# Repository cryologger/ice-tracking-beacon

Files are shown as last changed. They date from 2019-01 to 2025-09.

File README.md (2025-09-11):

# Cryologger - Iceberg Tracking Beacon (ITB)





### Note: This project is under active development. 



## 1.0 Introduction
Icebergs and ice islands represent significant hazards to marine navigation and offshore infrastructure at a time when demand for access to Canada’s Arctic waters is increasing. There is a growing demand for in situ iceberg tracking data to monitor their drift trajectory and improve predictions of ice hazard occurrence and behaviour, yet the high cost of commercial tracking devices often prevents monitoring at optimal spatial and temporal resolutions.

The Cryologger Ice Tracking Beacon (ITB), built using inexpensive, open-source hardware and software, provides a reliable and cost-effective platform for monitoring the drift of icebergs and ice islands in the Canadian Arctic.

## 2.0 Methods

### 2.1 Design

The Cryologger ITB is based on the open-source Arduino platform (www.arduino.cc) and built using low-cost, do-it-yourself electronics that can be easily modified to meet the needs of the end-user. Code was written using the Arduino Integrated Development Environment (IDE) and benefits from the availability of community-generated libraries.

Planned for extended deployments in harsh Arctic conditions, the Cryologger ITB provides long-term measurements of GNSS position, temperature, pressure, pitch, roll, tilt-compensated heading and battery voltage. Data are transmitted over the Iridium satellite network at specified intervals and can be remotely updated based on the desired sampling frequency. Collected data are made available in near-real time at https://cryologger.org.

#### 2.1.1 Design Iterations

More information about the design of versions 1.0 and 2.0 of the Cryologger ITB can be found in the following publication:

[Garbo, A., & Mueller, D. (2024). Cryologger Ice Tracking Beacon: A Low-Cost, Open-Source Platform for Tracking Icebergs and Ice Islands. _Sensors_, _24_(4), Article 4. https://doi.org/10.3390/s24041044](https://www.mdpi.com/1424-8220/24/4/1044)

Version 3.0 of the Cryologger ITB builds on the successes of previous versions and features a number of improvements to the design, including:
* 3.3 V power is now provided directly from a Pololu 3.3 V step-down voltage regulator, bypassing the Feather M0's onboard AP2112 LDO regulator (-55 μA).
* A dedicated 5 V step-down voltage regulator was added to power the RockBLOCK Iridium transceiver.
* The DS3231 real-time clock (RTC) was removed in favour of the SAMD21's internal RTC for all timekeeping and alarm functionality with periodic time synchronizations with the GPS.
* The LSM303 accelerometer/magnetometer was replaced with the LSM6DS33 + LIS3MDL IMU due to the sensor reaching its end-of-life (EOL).
* The temperature/pressure and IMU sensors are now powered directly through SAMD21 GPIO pins, allowing for power to be completely removed during sleep.
* A 10MΩ + 1 MΩ resistor divider is now used to measure the battery voltage (+2.4 μA).

A major change in v3.0 is a custom carrier board PCB that is designed to greatly simplify the assembly process. The PCB was designed in KiCad and fabricated by JLCPCB. 

  
<p align="center"><b>Figure 1:</b> 3D rendering of Cryologger iceberg drift tracking beacon carrier board designed in KiCad.</p>

#### 2.1.2 Bill of Materials (BOM)

**Table 1.** Bill of materials and associated costs for components used in the Cryologger ITB v3.1. Prices are listed in USD and are current as of December 2023. Taxes and shipping not included. <sup>1</sup>Denotes optional component. Please note BOM is a work in progress.
| Component | Product | Quantity | Cost (USD) |
| --- | --- | :---: | :---: |
| PCB | [Custom Cryologger Printed Circuit Board](https://jlcpcb.com) | 1 | $5.00 | 
| Satellite transceiver | [Rock7 RockBLOCK 9603](https://www.groundcontrol.com/us/product/rockblock-9603-compact-plug-and-play-satellite-transmitter/) | 1 | $267.50 |
| Satellite antenna<sup>1</sup> | [Maxtena M1621HCT-P-SMA](https://maxtena.com/products/f-passive/m1621hct-p-sma-iridium-passive-antenna/) | 1 | $54.00 |
| Microcontroller | [Adafruit Feather M0 Basic Proto](https://www.adafruit.com/product/2772) | 1 | $19.95 |
| GNSS Receiver | [Adafruit Ultimate GPS FeatherWing](https://www.adafruit.com/product/3133) | 1 | $24.95 |
| IMU | [Adafruit LSM303AGR Accelerometer Magnetometer](https://www.adafruit.com/product/4413) | 1 | $12.50 |
| Sensor | [Adafruit BME280 Temperature Humidity Pressure Sensor](https://www.adafruit.com/product/2652) | 1 | $14.95 |
| Voltage regulator | [Pololu D36V6F3 3.3V 600mA Step-Down Voltage Regulator](https://www.pololu.com/product/3791) | 1 | $6.95 |
| Voltage regulator | [Pololu D36V6F5 5V 600mA Step-Down Voltage Regulator](https://www.pololu.com/product/3792) | 1 | $6.95 |
| Resistor | [10 M 1% 0.6 W resistor](https://www.mouser.ca/ProductDetail/594-MBB02070C1005FCT) | 1 | $0.29 |
| Resistor | [1 M 1% 0.6 W resistor](https://www.mouser.ca/ProductDetail/594-B0207C1M000F5T) | 1 | $0.20 |
| Capacitor | [0.1 uF Capacitor](https://mou.sr/481ILov) | 1 | $0.23 |
| Power connector |	[Phoenix Contact MSTB 2,5/ 2-ST-5,08 - 1757019](https://mou.sr/47HAA0B) | 1 | $0.60 |
| Power connector	| [Phoenix Contact MSTBA 2,5/ 2-G-5,08 - 1757242](https://mou.sr/3R27Ick) | 1 | $1.81 |
| Connector |	[Molex PicoBlade PCB Header](https://mou.sr/3qLrmgc) | 1| $0.55 |
| Connector |	[Molex PicoBlade Crimp Housing](https://mou.sr/3lXOY2x])| 2| $0.36 |
| Cable Assembly |	Molex PicoBlade Pre-crimped Jumper Wires | 5 | |
| Enclosure | [Nanuk 904](https://nanukcases.ca/products/nanuk-904) | 1 | $47.95 |
| Battery | [Tadiran TLP93121](https://www.tadiranbat.com/assets/tlp-93121-b-al1.pdf) | 1 | $145.50 |
| **Total** | | | |

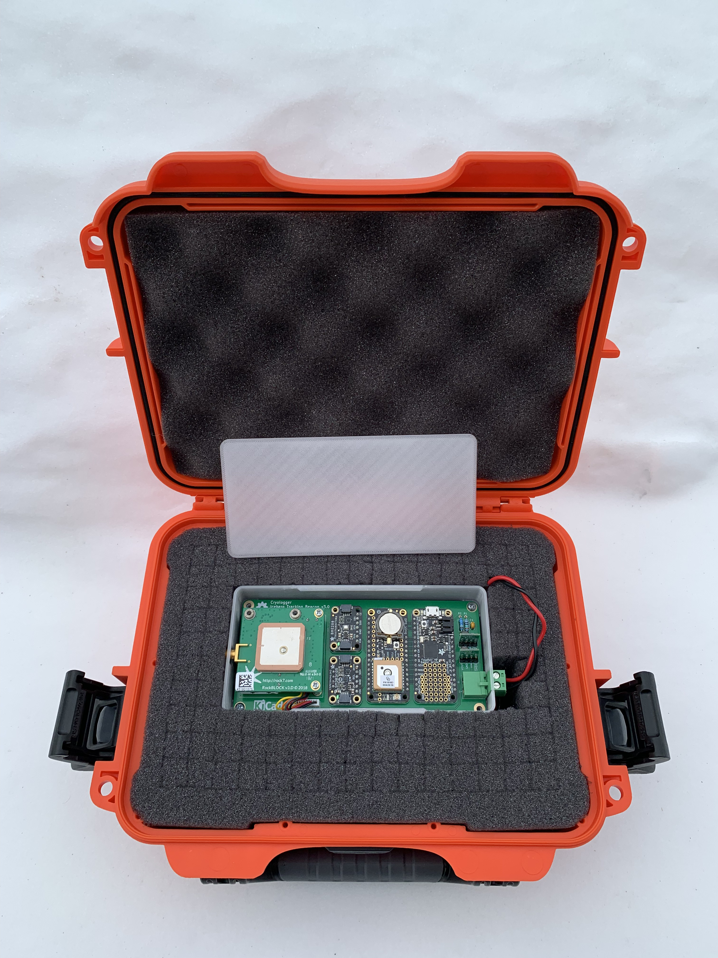
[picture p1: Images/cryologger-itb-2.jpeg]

<p align="center"><b>Figure 2:</b> Assembled Cryologger ice drift tracking beacon housed in Nanuk case and 3D-printed case lid removed.</p>

### 2.2 Operation

The programming logic of the Cryologger ITB optimizes sleep and wake cycles to minimize overall power consumption. When initially powered on, the system attempts to acquire a signal from the GNSS receiver and synchronizes the RTC with the current date and time. It then sets an alarm for the initial sampling interval and enters a low-power, deep-sleep mode. When the alarm triggers, the system wakes, records the time, and acquires a GNSS position. Next, measurements of all onboard sensors are collected (Table 2). These data are stored into memory and when the software determines the appropriate transmission interval has been met, it attempts to transmit the data using the RockBLOCK satellite transceiver. The software then disables power to all components, sets the next alarm, and returns to sleep.

#### 2.2.1 Measurements

**Table 2.** Measurements recorded and transmitted by the Cryologger ITB v3.0, including variable sizes.
|     Variable             |     Unit    |     Description                                   |     Size (bytes)    |
|--------------------------|-------------|---------------------------------------------------|---------------------|
|     unixtime             |     s       |     Unix time (seconds since 1970-01-01)          |     4               |
|     temperature_int      |     °C      |     Internal temperature                          |     2               |
|     humidity_int         |     %       |     Internal humidity                             |     2               |   
|     pressure_int         |     hPa     |     Internal pressure                             |     2               |   
|     pitch                |     °       |     Pitch angle                                   |     2               |   
|     roll                 |     °       |     Roll angle                                    |     2               |   
|     heading              |     °       |     Tilt-compensated magnetic heading (0-360°)    |     2               |   
|     latitude             |     °       |     GNSS latitude                                 |     4               |   
|     longitude            |     °       |     GNSS longitude                                |     4               |   
|     satellites           |             |     Number of GNSS satellites in view             |     2               |   
|     hdop                 |             |     GNSS horizontal dilution of precision         |     2               |   
|     voltage              |     V       |     Battery voltage                               |     2               |   
|     transmit_duration    |     s       |     Transmission time of SBD message              |     2               |   
|     transmit_status      |             |     Iridium return code                           |     1               |   
|     message_counter      |             |     Number of transmitted messages                |     2               |   

#### 2.2.2 Data Transmission and Processing

The Cryologger ITB records its position and sensor measurements nominally on an hourly basis and transmits at an interval of 3 hours. Data are transmitted via the Iridium satellite network as a Short Burst Data (SBD) message. The ITB attempts to transmit each message for up to 180 seconds, and if unsuccessful, the message is stored in a temporary buffer and reattempted at the next transmission interval. Both the sampling and transmission frequency of individual Cryologgers can be remotely modified by the end-user. Successfully transmitted SBD messages are received by an Iridium ground station and sent to Ground Control's server. These data are then forwarded to Amazon Web Services (AWS), where they are decoded using a Python script, stored in a database, and visualized on the Cryologger website: https://cryologger.org.

## 3.0 Deployments

A total of 37 Cryologger ITBs have been deployed between 2018 and 2023 (Figure 3), primarily during the annual Amundsen Expedition. Deployments are performed by helicopter from the CCGS Amundsen on icebergs and ice islands along the coasts of Ellesmere Island, Baffin Island and Greenland (Figure 3). At the time of deployment, a compass heading of the tracking beacon was recorded. Where possible, a 360° aerial photo survey of the iceberg was performed for use with Structure-from-Motion photogrammetry to create 3D models of the iceberg.

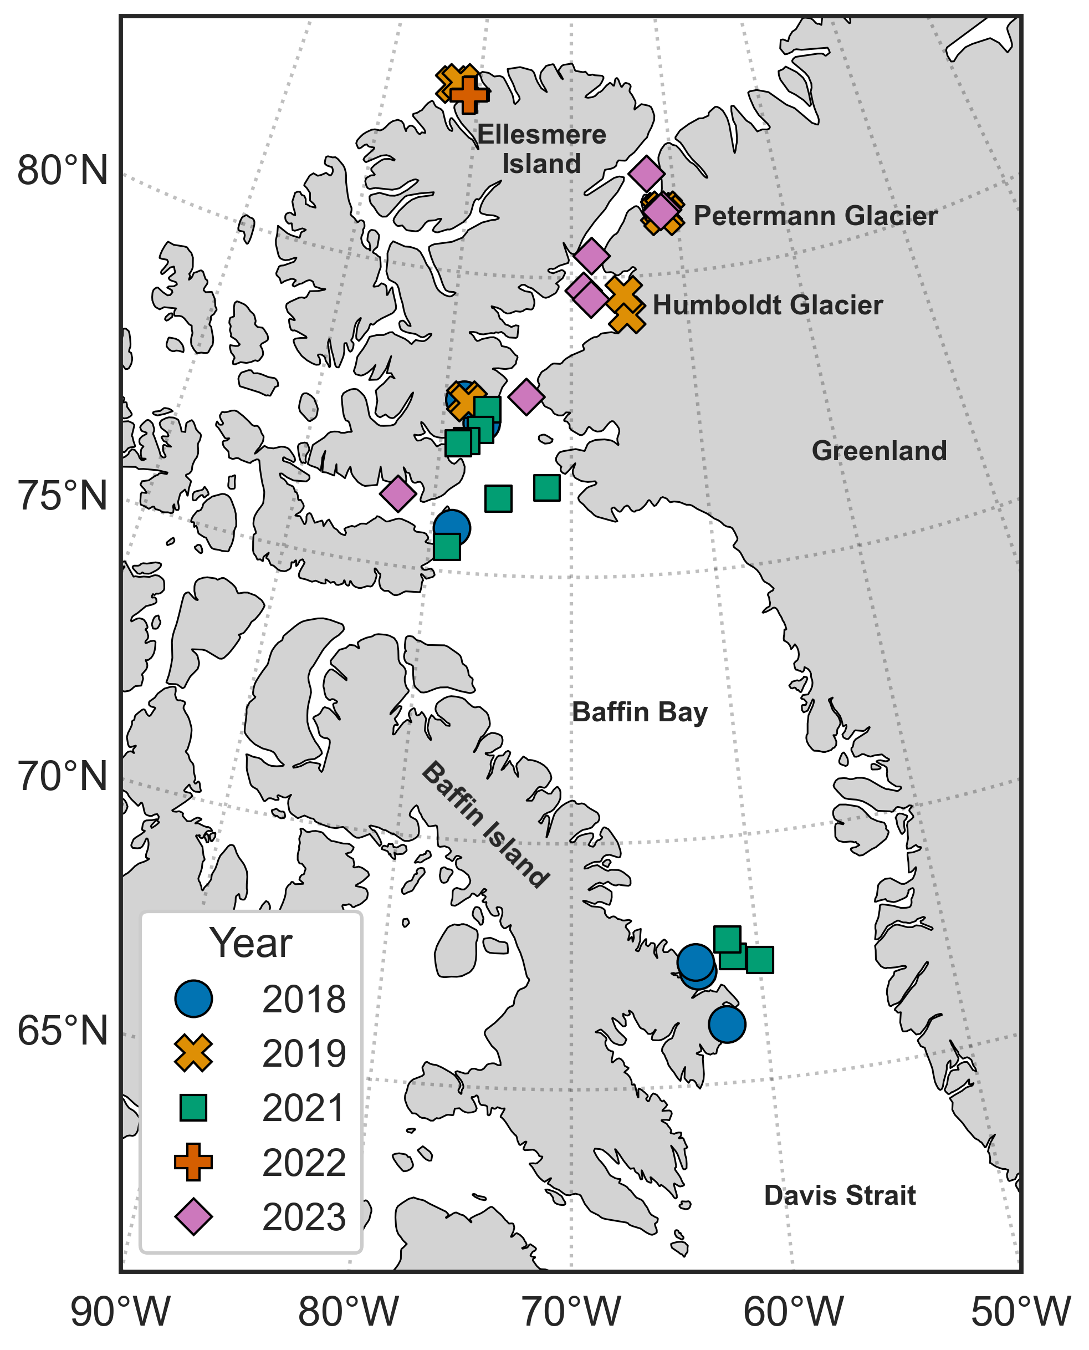
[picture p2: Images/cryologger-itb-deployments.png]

<p align="left"><b>Figure 3:</b> Map of Cryologger ice drift tracking beacons deployed between 2018 and 2023.</p>

The overall suitability of potential targets was determined by assessing the iceberg’s size, shape, and location. Where possible, icebergs selected to be instrumented with a tracking beacon were large enough to survive drifting south to the Grand Banks of Newfoundland and far enough away from the coast to increase the chances of being carried southward by the currents and avoid becoming grounded in shallow coastal areas. 

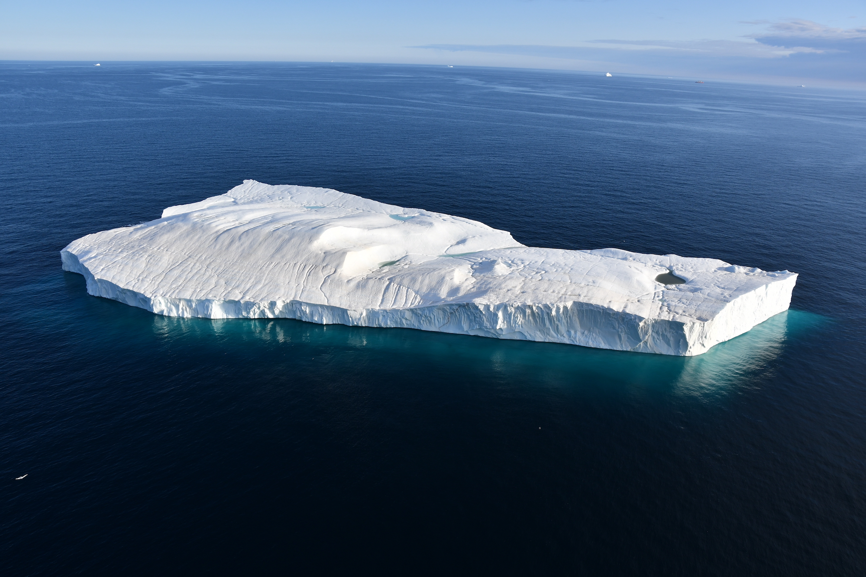
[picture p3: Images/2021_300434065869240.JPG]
<p align="center">
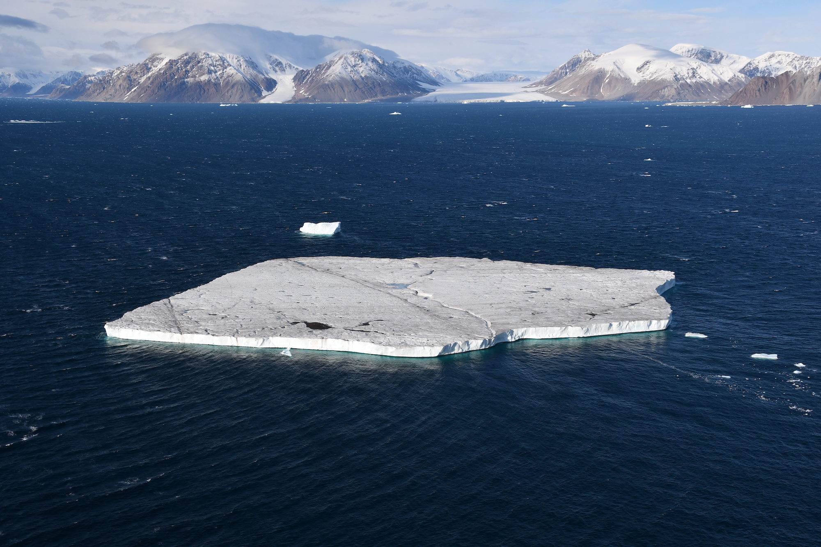
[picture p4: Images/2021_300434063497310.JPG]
</p>
<p align="center">
</p>
<p align="center"><b>Figure 4:</b> Examples of icebergs instrumented with Cryologger iceberg tracking beacons during the 2021 Amundsen Expedition.</p>

## 4.0 Results

The operation of the Cryologger ITBs greatly exceeded expectations, with the operational lifespans of deployments made in 2018 ranging from 310 to 1530 days, and those in 2019 ranging from 333 to 615 days. The most frequent causes of loss of communication with the ITBs was due to the eventual deterioration (calving or rolling) or catastrophic break-up of the iceberg and subsequent destruction of the beacon. In many cases, it was possible to use remote sensing imagery to observe major break-up events of icebergs that immediately resulted in transmissions from the beacon ceasing.

### 4.1 Iceberg Drift
A snapshot of iceberg drift tracks recorded from all Cryologger ITB deployments as of December 2023 is shown in Figure 4. This data can also be viewed in real-time at: https://cryologger.org/tracking


<p align="center"><b>Figure 5:</b> Map of Cryologger iceberg drift track tracks from beacons deployed between 2018 and 2023.</p>

## 5.0 Conclusion

The overall success of the Cryologger ITB has demonstrated that it can provide a robust platform for the collection of in-situ iceberg tracking data. With a total cost of approximately $700 USD in materials each, this represents a cost-effective alternative to existing proprietary commercial systems. 

The development and deployment of these novel iceberg tracking beacons were intended to enhance and supplement existing iceberg observation networks within the Canadian Arctic and data collected from the Cryologgers has already contributed to a database of iceberg tracking beacon tracks compiled by the Canadian Ice Service (CIS). Most importantly, this research demonstrates to the scientific community that inexpensive, open-source hardware and software can provide a viable solution for the monitoring of icebergs and ice island drift patterns within the Canadian Arctic and beyond!

Development of the next iteration of the Cryologger ITB is currently underway, which is focused on improving overall reliability, exploring the use of environmentally friendly materials, and improvements that will allow it to transform into an ocean drifter buoy once the breakup of the icebergs occurs. 

## Repository Contents

* **/Documentation** - Assembly, deployment and troubleshooting guides, as well as information on components used and associated costs.

* **/Hardware** - KiCad PCB schematic and design files.

* **/Software** -  Arduino code and Python data analysis scripts.

## License Information
Cryologger code, firmware, and software is licensed under the GNU General Public License v3.0 (https://www.gnu.org/licenses/gpl-3.0.en.html). 

<p xmlns:cc="http://creativecommons.org/ns#" >Cryologger hardware is licensed under <a href="https://creativecommons.org/licenses/by-nc-sa/4.0/?ref=chooser-v1" target="_blank" rel="license noopener noreferrer" style="display:inline-block;">CC BY-NC-SA 4.0 </a></p>

Cheers,

**Adam Garbo**

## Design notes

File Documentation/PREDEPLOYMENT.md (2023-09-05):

# Cryologger Ice Tracking Beacon (ITB) - Pre-Deployment
This guide provides step-by-step instructions on preparing the Cryologger ITBs for deployment.

## System Description:

The Cryologger ITB consists of a water-resistant Nanuk case, which contains the battery and electronics. The electronics are housed in a 3D-printed enclosure. 

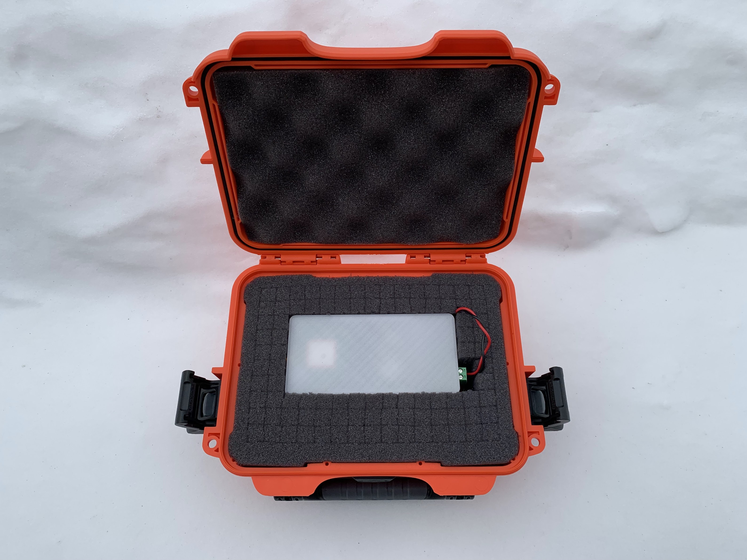
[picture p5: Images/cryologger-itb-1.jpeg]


## Pre-Deployment Checklist

### Install Software
* Ensure all steps were followed in [INSTALLATION.md](https://github.com/adamgarbo/cryologger-ice-tracking-beacon/blob/main/Documentation/INSTALLATION.md) to install the necessary Arduino IDE software and related libraries.

### Unpack Equipment
- Inspect the Cryologger ITBs for any potential damage to the Nanuk enclosures, electronics and batteries.

### Assemble Battery
The Cryologger ITB uses a 7.2 V 38 Ah lithium thionyl chloride (Li-SoCl2) battery. The battery is not terminated from the factory and requires a Phoenix Contact PCB connector to be attached.  
**Warning:** This battery has an extremely high energy density and care must be given to avoid shorting the black and red wires.

- Begin by stripping approximately 7 mm from the end of the red (+) and black (-) wires
- Insert each wire into the Phoenix Contact PCB connector one at a time
- Tighten the screw using sufficient force to ensure the wire cannot be pulled out of the connector
- Ensure no bare wire can be seen sticking out of the PCB connector
- Triple check that the red (+/right) and black (-/left) wires are in the correct positions before plugging in the battery.
  - The PCB is also marked with -/+ and can be used to confirm the correct orientation.
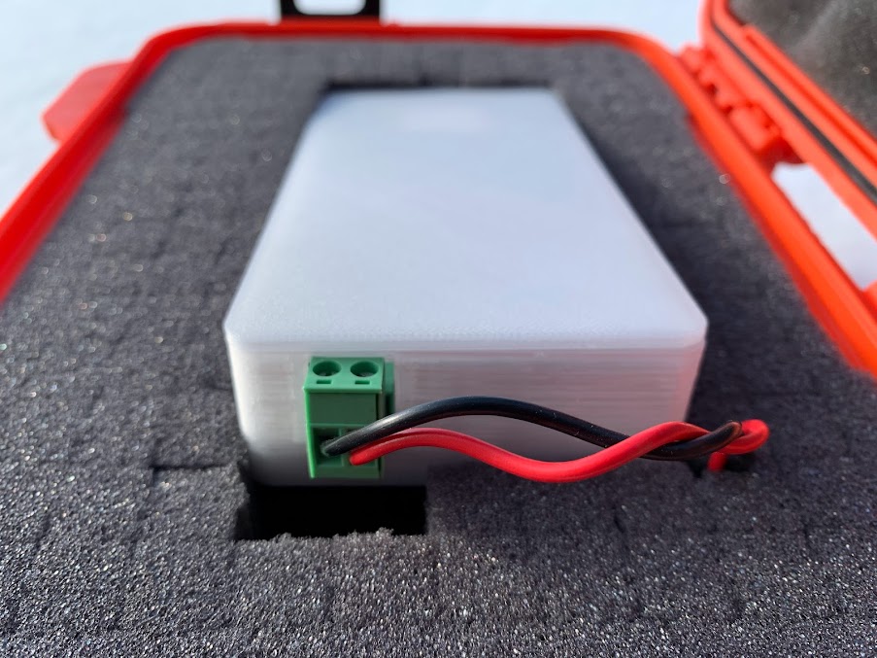
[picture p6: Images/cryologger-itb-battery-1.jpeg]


### Assemble Wooden Platform

## Testing

### Initial Test & Documentation
The first step is conduct a test of each Cryologger ITB to ensure it can properly transmit a message. It is advantageous to document the operation of each Cryologger at the same time in order to better troubleshoot any issues that may be encoutnered.

- Launch the Arduino IDE
- Connect to the ITB using a mini-USB cable
- Connect the battery to the ITB
- Open the Serial Monitor in Arduino IDE
- Observe the serial output as the Cryologger initalizes its sensors and attempts an initial transmission
- Once the transmission is complete, copy the complete the serial output to a .txt file 
  - Use the format: `cryologger_itb_2023_X.txt`, where X is the unit number of the Cryologger
- Also Note the presenece of any errors encountered and report them as soon as possible

### Long-Duration Test
Next, a long-duration test of all of the Cryologger ITBs can be conducted. This is an important step to ensure their proper operation prior to deployment. The tests should be run for a minimum of 24 hours and ideally can continue for up to 1 week. 
- Place the ITBs in an area with a good view of the sky
- Secure the ITBs they do not roll or blow away using a rope to lash all Nanuk enclosures together, and then tied off to the deck of the ship
<p align="center">
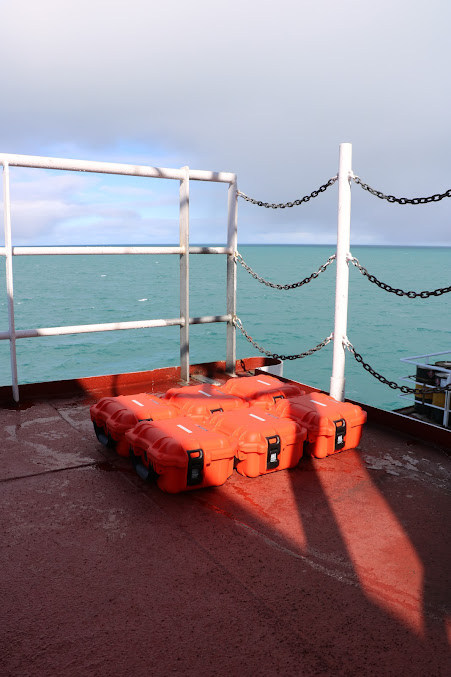
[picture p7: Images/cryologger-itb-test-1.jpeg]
  
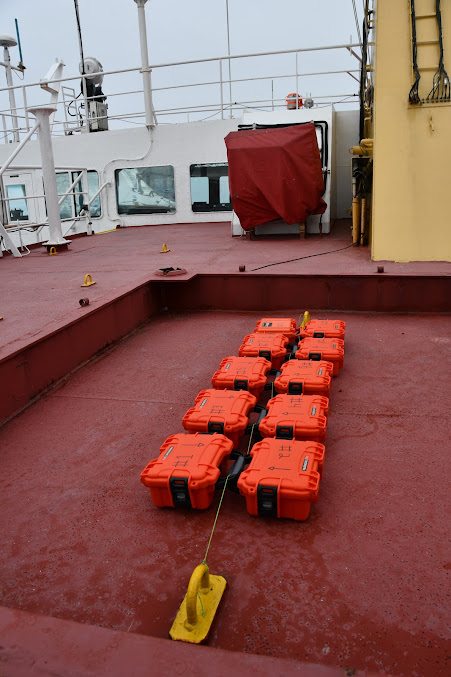
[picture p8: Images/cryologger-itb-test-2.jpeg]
  
</p>

- Power on each ITB one at a time and observe the LED blink patterns
- Document the time each Cryologger is turned on.
- Review the data on the Cryologger website: https://cryologger.org/amundsen-2023

## Troubleshooting
Document any issues that arise so that they can be addressed as needed.

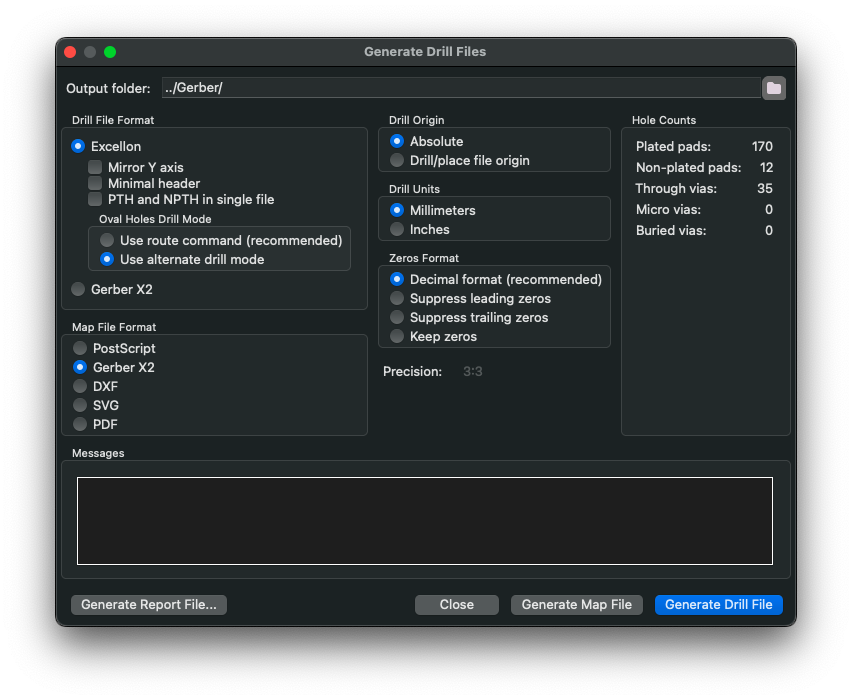
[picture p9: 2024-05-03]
Hardware/Gerber/drill-settings.png

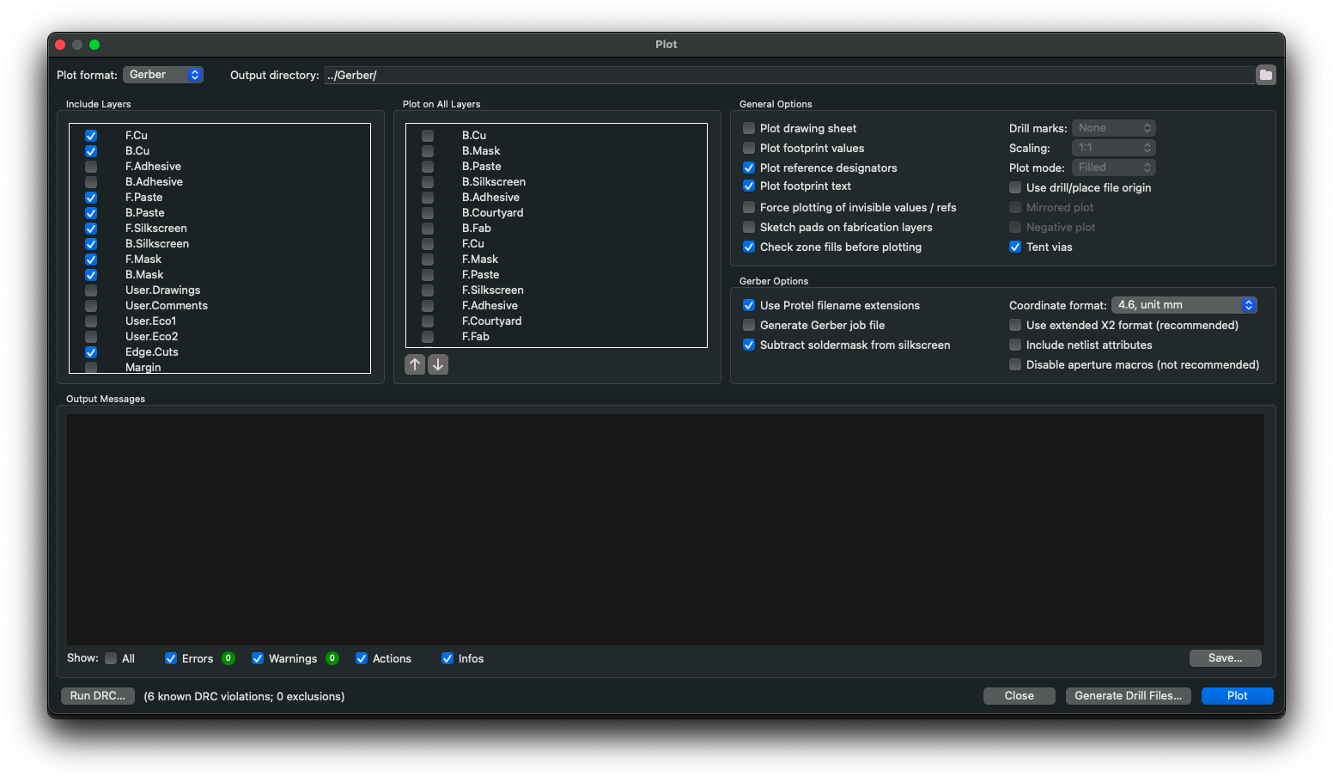
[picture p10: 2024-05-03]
Hardware/Gerber/plot-settings.png

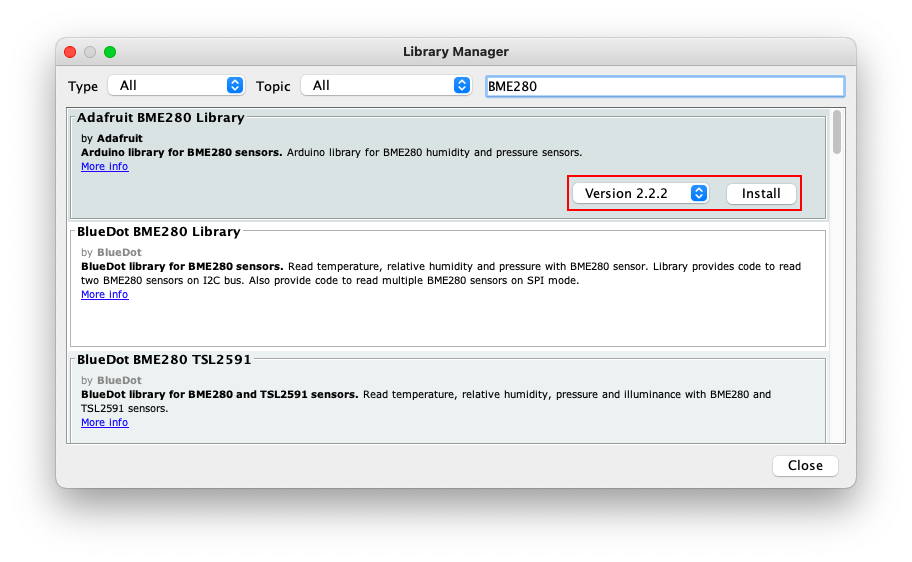
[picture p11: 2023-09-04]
Images/arduino-ide-library.png

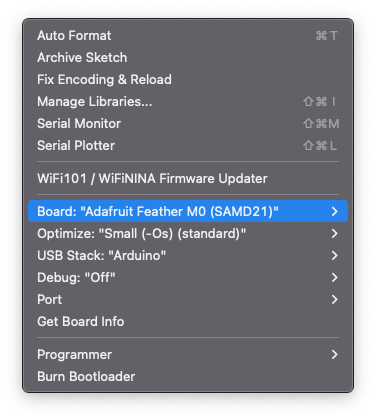
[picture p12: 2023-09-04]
Images/arduino-ide-board-1.png

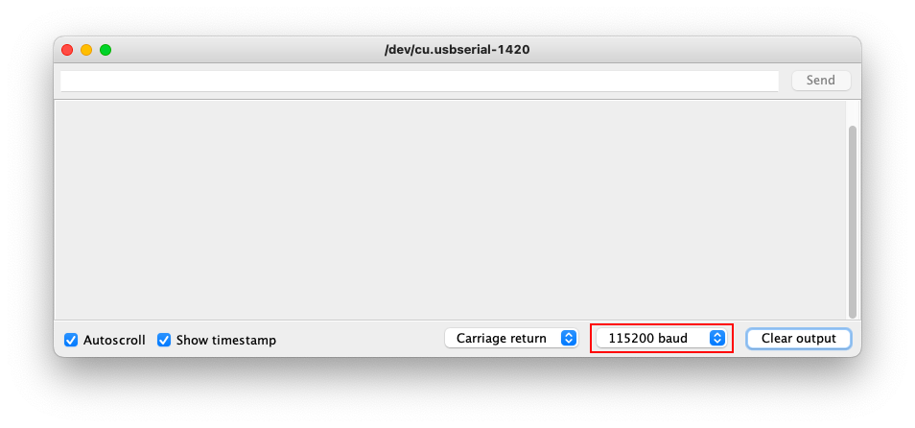
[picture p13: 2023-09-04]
Images/arduino-ide-serial-monitor-2.png

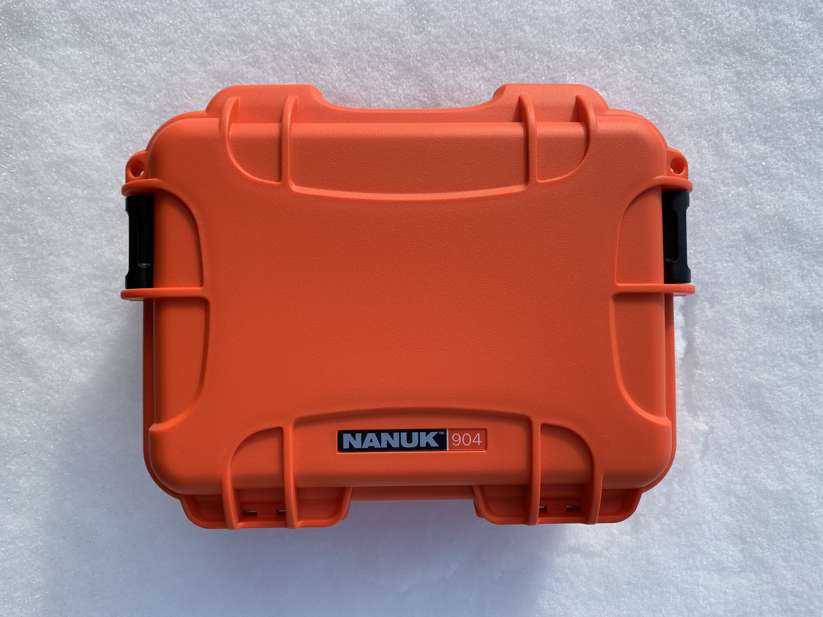
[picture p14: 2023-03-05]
Images/cryologger-itb-3.jpeg

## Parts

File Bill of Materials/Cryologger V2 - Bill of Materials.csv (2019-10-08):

Component | Manufacturer | Product | Quantity | URL
Satellite modem | Rock Seven | RockBLOCK 9603 | 1 | http://www.rock7mobile.com/products-rockblock-9603
Microcontroller | Adafruit | Feather M0 Basic Proto | 1 | https://www.adafruit.com/product/2772
GPS | Adafruit | Ultimate GPS FeatherWing | 1 | https://www.adafruit.com/product/3133
Accelerometer/Magnetometer | Pololu | LSM303D 3D Compass and Accelerometer Carrier with Voltage Regulator | 1 | https://www.pololu.com/product/2127
Real-time clock (RTC) | Adafruit | DS3231SN RTC FeatherWing | 1 | https://www.adafruit.com/product/3028
Real-time clock battery | Adafruit | CR1220 12mm Diameter - 3V Lithium Coin Cell Battery | 2 | https://www.adafruit.com/product/380
Step-down voltage regulator | Pololu | 3.3V, 600mA Step-Down Voltage Regulator D36V6F3 | 1 | https://www.pololu.com/product/3791
Power connector | Adafruit | Male DC Power adapter - 2.1mm plug to screw terminal block | 1 | https://www.adafruit.com/product/369
Power connector | Adafruit | Breadboard-friendly 2.1mm DC barrel jack | 1 | https://www.adafruit.com/product/373
PCB | Adafruit | FeatherWing Tripler | 1 | https://www.adafruit.com/product/3417
Terminal block | Adafruit | 2.54mm/0.1" Pitch Terminal Block - 5-pin | 1 | https://www.adafruit.com/product/2139
Battery | Tadiran | Lithium Pulses Plus 7.2V 38Ah 273.6Wh (TLP-93131/B/AL1) | 1 | http://www.tadiranbat.com/assets/tlp-93121-b-al1.pdf
Case | Nanuk | Nanuk 903 Small series | 1 | https://www.nanuk.com/nanuk-904.php

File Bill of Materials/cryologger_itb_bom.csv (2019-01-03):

Component | Manufacturer | Product | Quantity | Cost ($USD) | Cost (£GPB) | Cost ($CAD) | URL
Satellite modem | Rock Seven | RockBLOCK 9603 | 1 |  | £143.10 | $243.27 | http://www.rock7mobile.com/products-rockblock-9603
Satellite modem antenna | Maxtena | M1600HCT-P-SMA | 1 | $67.69 |  | $88.00 | http://www.richardsonrfpd.com/pages/Product-Details.aspx?productId=1142189
Microcontroller | Adafruit | Pro Trinket - 3V 12MHz | 1 | $9.95 |  | $12.94 | https://www.adafruit.com/products/2010
GPS | Adafruit | Ultimate GPS Breakout - 66 channel w/10 Hz updates - Version 3 | 1 | $39.95 |  | $51.94 | https://www.adafruit.com/products/746
EEPROM | Microchip | 256K I2C EEPROM 24LC256 | 1 | $1.95 |  | $2.54 | https://www.sparkfun.com/products/525
Accelerometer/Magnetometer | Adafruit | LSM303 - Triple-axis Accelerometer + Magnetometer (Compass) Board | 1 | $14.95 |  | $19.44 | https://www.adafruit.com/products/1120
Temperature/Pressure Sensor | Adafruit | MPL3115A2 - I2C Barometric Pressure/Altitude/Temperature Sensor | 1 | $9.95 |  | $12.94 | https://www.adafruit.com/product/1893
Real-time clock IC | Maxim | DS3231SN | 1 |  |  | $14.91 | https://www.digikey.ca/product-detail/en/maxim-integrated/DS3231SN-T-R/DS3231SN-T-RCT-ND/3894827
Real-time clock PCB | Adafruit | SMT Breakout PCB for SOIC-16 | 1 | $1.32 |  | $1.71 | https://www.adafruit.com/product/1207
Real-time clock battery | Adafruit | 20mm Coin Cell Breakout Board (CR2032) | 1 | $2.50 |  | $3.25 | https://www.adafruit.com/product/1870
Step-down voltage regulator | Pololu | 5V, 2.5A Step-Down Voltage Regulator D24V22F5 | 1 | $8.95 |  | $11.64 | https://www.pololu.com/product/2858
Power connector | Adafruit | Male DC Power adapter - 2.1mm plug to screw terminal block | 1 | $2.00 |  | $2.60 | https://www.adafruit.com/product/369
Power connector | Adafruit | Breadboard-friendly 2.1mm DC barrel jack | 1 | $0.95 |  | $1.24 | https://www.adafruit.com/product/373
Connector | Molex | SL PCB Header | 1 |  |  | $1.49 | https://www.digikey.ca/product-detail/en/molex-connector-corporation/0705430040/WM4828-ND/313743
PCB | Adafruit | Perma-Proto Full-sized Breadboard PCB - Single | 1 | $5.95 |  | $7.74 | https://www.adafruit.com/product/1606
Battery | Adafruit | CR2032 Lithium Coin Cell Battery | 1 | $0.95 |  | $1.24 | https://www.adafruit.com/product/654
Battery | Tadiran | Lithium Pulses Plus 7.2V 38Ah 273.6Wh (TLP-93131/B/AL1) | 1 |  |  | $146.45 | http://www.tadiranbat.com/assets/tlp-93121-b-al1.pdf
Case | Nanuk | Nanuk 905 | 1 |  |  | $64.75 | https://www.nanuk.com/nanuk-905.php
 |  |  |  |  | Total | $688.04

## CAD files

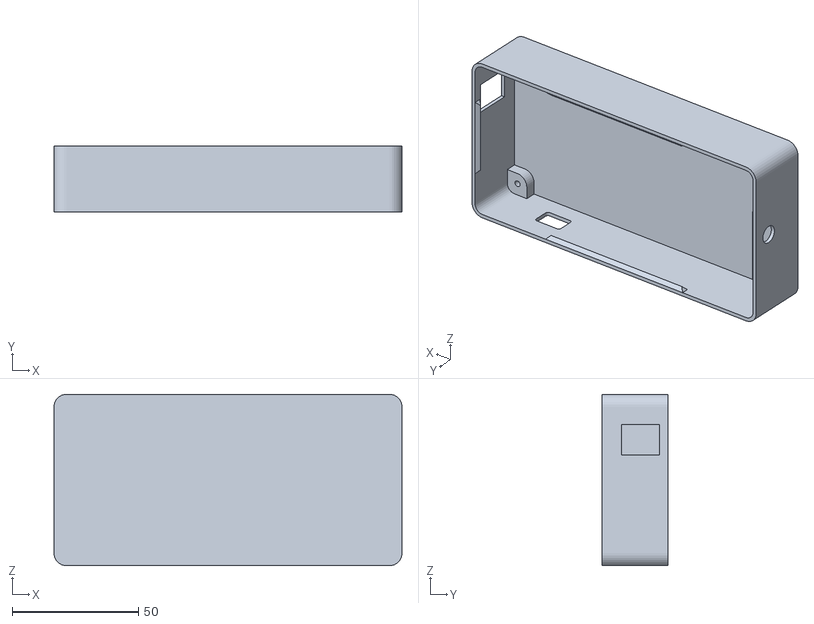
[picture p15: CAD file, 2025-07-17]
Hardware/3D Printing/case_v3.2.stl
138.0 x 26.0 x 68.0

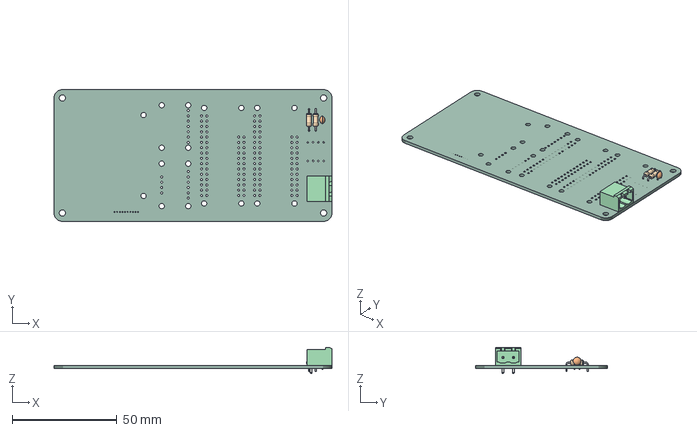
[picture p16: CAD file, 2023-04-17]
Hardware/KiCad/Cryologger ITB.step
133.0 x 63.0 x 12.6 mm
PCB

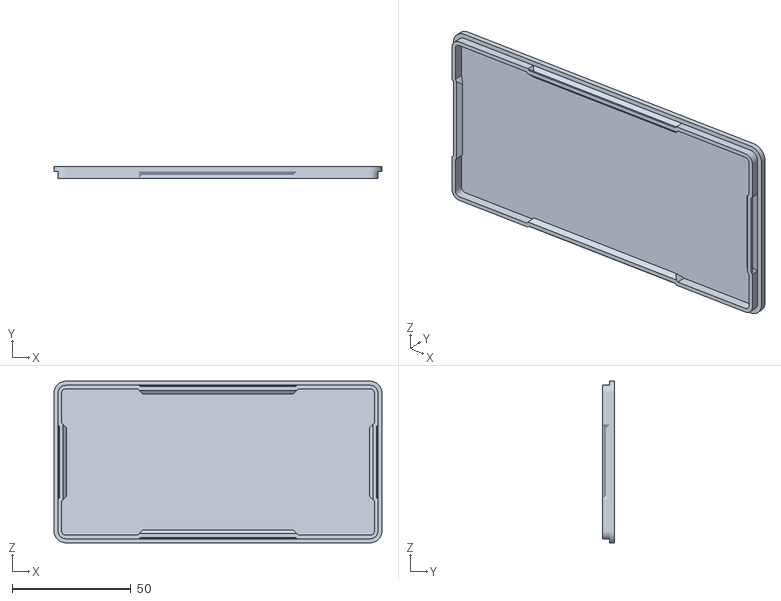
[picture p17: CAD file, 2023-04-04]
Hardware/3D Printing/cover_v3.1.stl
138.0 x 5.00 x 68.0

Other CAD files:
Hardware/3D Printing/case_v3.1.stl

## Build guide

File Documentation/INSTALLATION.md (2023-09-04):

# Cryologger Ice Tracking Beacon (ITB) - Installation
This guide provides step-by-step instructions on installing the Arduino IDE and required board definitions and libraries, which are necessary for uploading code to the Cryologger ITB.

## Step 1: Download Arduino IDE  
* Navigate to https://www.arduino.cc/en/software and download the Legacy 1.8.x version of the Arduino IDE
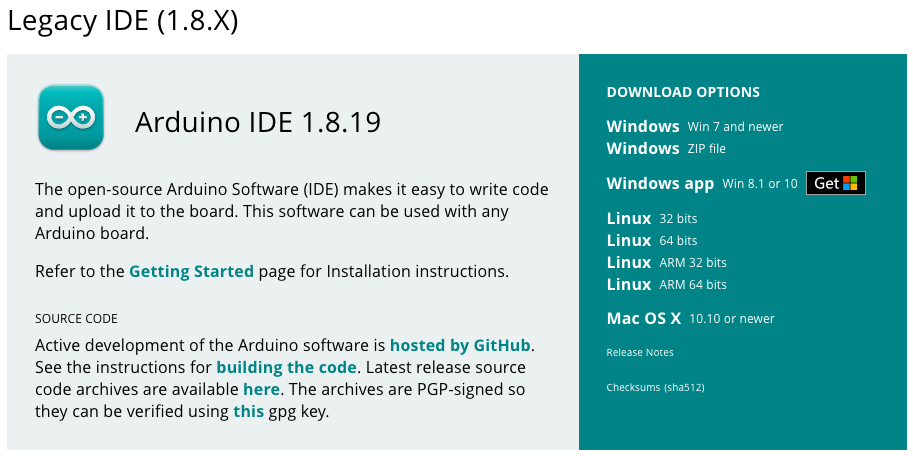
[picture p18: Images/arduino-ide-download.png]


## Step 2: Add Additional Boards Manager URL:
* In the Arduino IDE navigate to: Preferences
* Add the following "Additional Boards Manager URL" as shown in the screenshot below:  
```https://adafruit.github.io/arduino-board-index/package_adafruit_index.json```
* Also during this step, check the "compile" and "upload" boxes for "Show verbose output during" and change "Compiler warnings" to "Default"
![image](/Images/arduino-ide-preferences.png)

## Step 3: Install Board Definitions
* Navigate to: Tools > Boards > Boards Manager
* Search for: SAMD Boards
* Select and install version: Arduino SAMD Boards v1.8.13 
* Select and install version: Adafruit SAMD Boards v1.7.13
![image](/Images/arduino-ide-boards.png)

## Step 4: Install Libraries
Several libraries are required by the Cryologger ITB. These can be downloaded using the Arduino IDE's Library Manager (requires an Internet connection).

* Navigate to: Tools > Manage Libraries
* Search for and install the following libraries:

**Table 1.** Libraries required by Cryologger ITB. Last updated 2023-06-19.
| Library                 | Version | GitHub Repository                                                   |
|-------------------------|---------|---------------------------------------------------------------------|
| Adafruit BME280         | 2.2.2   | https://github.com/adafruit/Adafruit_BME280_Library                 |
| Adafruit LSM303 Accel   | 1.1.6   | https://github.com/adafruit/Adafruit_LSM303_Accel                   |
| Adafruit LIS2MDL        | 2.1.4   | https://github.com/adafruit/Adafruit_LIS2MDL                        |
| Adafruit Unified Sensor | 1.1.9   | https://github.com/adafruit/Adafruit_Sensor                         |
| Arduino Low Power       | 1.2.2   | https://github.com/arduino-libraries/ArduinoLowPower                |
| IridiumSBD              | 3.0.6   | https://github.com/sparkfun/SparkFun_IridiumSBD_I2C_Arduino_Library |
| RTCZero                 | 1.6.0   | https://github.com/arduino-libraries/RTCZero                        |
| TimeLib                 | 1.6.1   | https://github.com/PaulStoffregen/Time                              |
| TinyGPSPlus             | 1.0.3   | https://github.com/mikalhart/TinyGPSPlus                            |

![image](/Images/arduino-ide-library.png)

## Step 5: Download Software
Code for the Cryologger ITB is made available on the following GitHub repository:
* [https://github.com/adamgarbo/Cryologger Ice_Tracking_Beacon](https://github.com/adamgarbo/Cryologger_Ice_Tracking_Beacon)
* Click on "Releases" and download the .zip file of the most recent release:

## Step 6: Test Program Compilation
* Navigate to the /Software/Arduino/cryologger_itb folder of the downloaded repository
* Double-click on the `cryologger_aws.ino` file
* Click on the checkmark in the upper left corner of the Arduino IDE program window
* Watch debugging window for compilation errors

![image](/Images/arduino-ide-verify.png)

## Step 7: Connect Hardware & Configure Port Settings
* Connect to the Cryologger ITB using a micro USB cable.
* In the Arduino IDE click on Tools > Board > Adafruit SAMD > Adafruit Feather M0 (SAMD)

![image](/Images/arduino-ide-board-1.png)
![image](/Images/arduino-ide-board-2.png)
![image](/Images/arduino-ide-board-3.png)

* Next, click on Tools > Port and select the appropriate serial port for the Adafruit Feather M0 Adalogger
![image](/Images/arduino-ide-port-1.png)
![image](/Images/arduino-ide-port-2.png)

## Step 8: Upload Program
* Once the code has compiled successfully, click on the right-pointed arrow to upload the code
* Watch the output window for compilation errors and/or success messages
* If no errors are presented, the code has now been successfully uploaded! 
![image](/Images/arduino-ide-upload.png)

## Step 9: Observe Serial Monitor
* After successfully uploading the program, click on the magnifying glass in the top right-hand corner to open the Serial Monitor
* Click on the baud dropdown and select 115200 baud
* Ensure the data logging mode and settings are correct
![image](/Images/arduino-ide-serial-monitor-1.png)
![image](/Images/arduino-ide-serial-monitor-2.png)

## Step 10: Next Steps
* The detailed operation of the Cryologger ITB will be covered next in OPERATION.md

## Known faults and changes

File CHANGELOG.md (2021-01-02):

# Changelog:

November, 2020
 * Added Qwiic Power Switch to control power to components with high current consumption (e.g. u-blox SAM-M8Q, ICM-20948). 
 * The SparkFun Buck-Boost Converter power the 3.3 V bus directly. ~110-141 uA in sleep mode (total) at 7.4 - 12.5 V

November 18, 2020
* Initial prototype tests performed.

December 20, 2020
* The decision was made to abandon the MicroMod-based beacon prototype. While the MicroMod ecosystem has potential, at present the MicroMod Data Logging Carrier Board (MMDLC) coupled with the Artemis Processor presents a number of significant hardware bugs (i.e. ADC, voltage divider) and a considerably high quiescent draw of ~300 uA.

December 28, 2020
* Removed all SparkX components from design (i.e. Qwiic Power Switch/Qwiic Iridium 9603N) due to concern of being able to reliably source components in the future (i.e. no stock, no longer producing).

December 29, 2020
* Added Qwiic RV-8803 RTC to address extreme clock drift experienced by the SparkFun Qwiic Micro due to lack of SAMD21 external RTC crystal.

December 30, 2020
* Added P-MOSFET to control power to perhipherals (e.g. GNSS, IMU, LED).

December 31, 2020
* Prototype tests performed. 
* Overall good results but neither the Buck-Boost or Pololu step-down regulator are capable of powering the RockBLOCK 9603 with 3.3 V on the 3.7 V LiIon pin. 
* Possible solutions include a dedicated 5.0 V regulator.

January 1, 2021
* Changed processing of incoming MT-SBD messages to use union/structure. 
* This will require that all MT messages be sent in little endian byte order.
* Measured quiescent draw of ~55 uA between Buck-Boost and 3.3 V rail in deep sleep.
* Regulator current will add ~60-130 uA depending.

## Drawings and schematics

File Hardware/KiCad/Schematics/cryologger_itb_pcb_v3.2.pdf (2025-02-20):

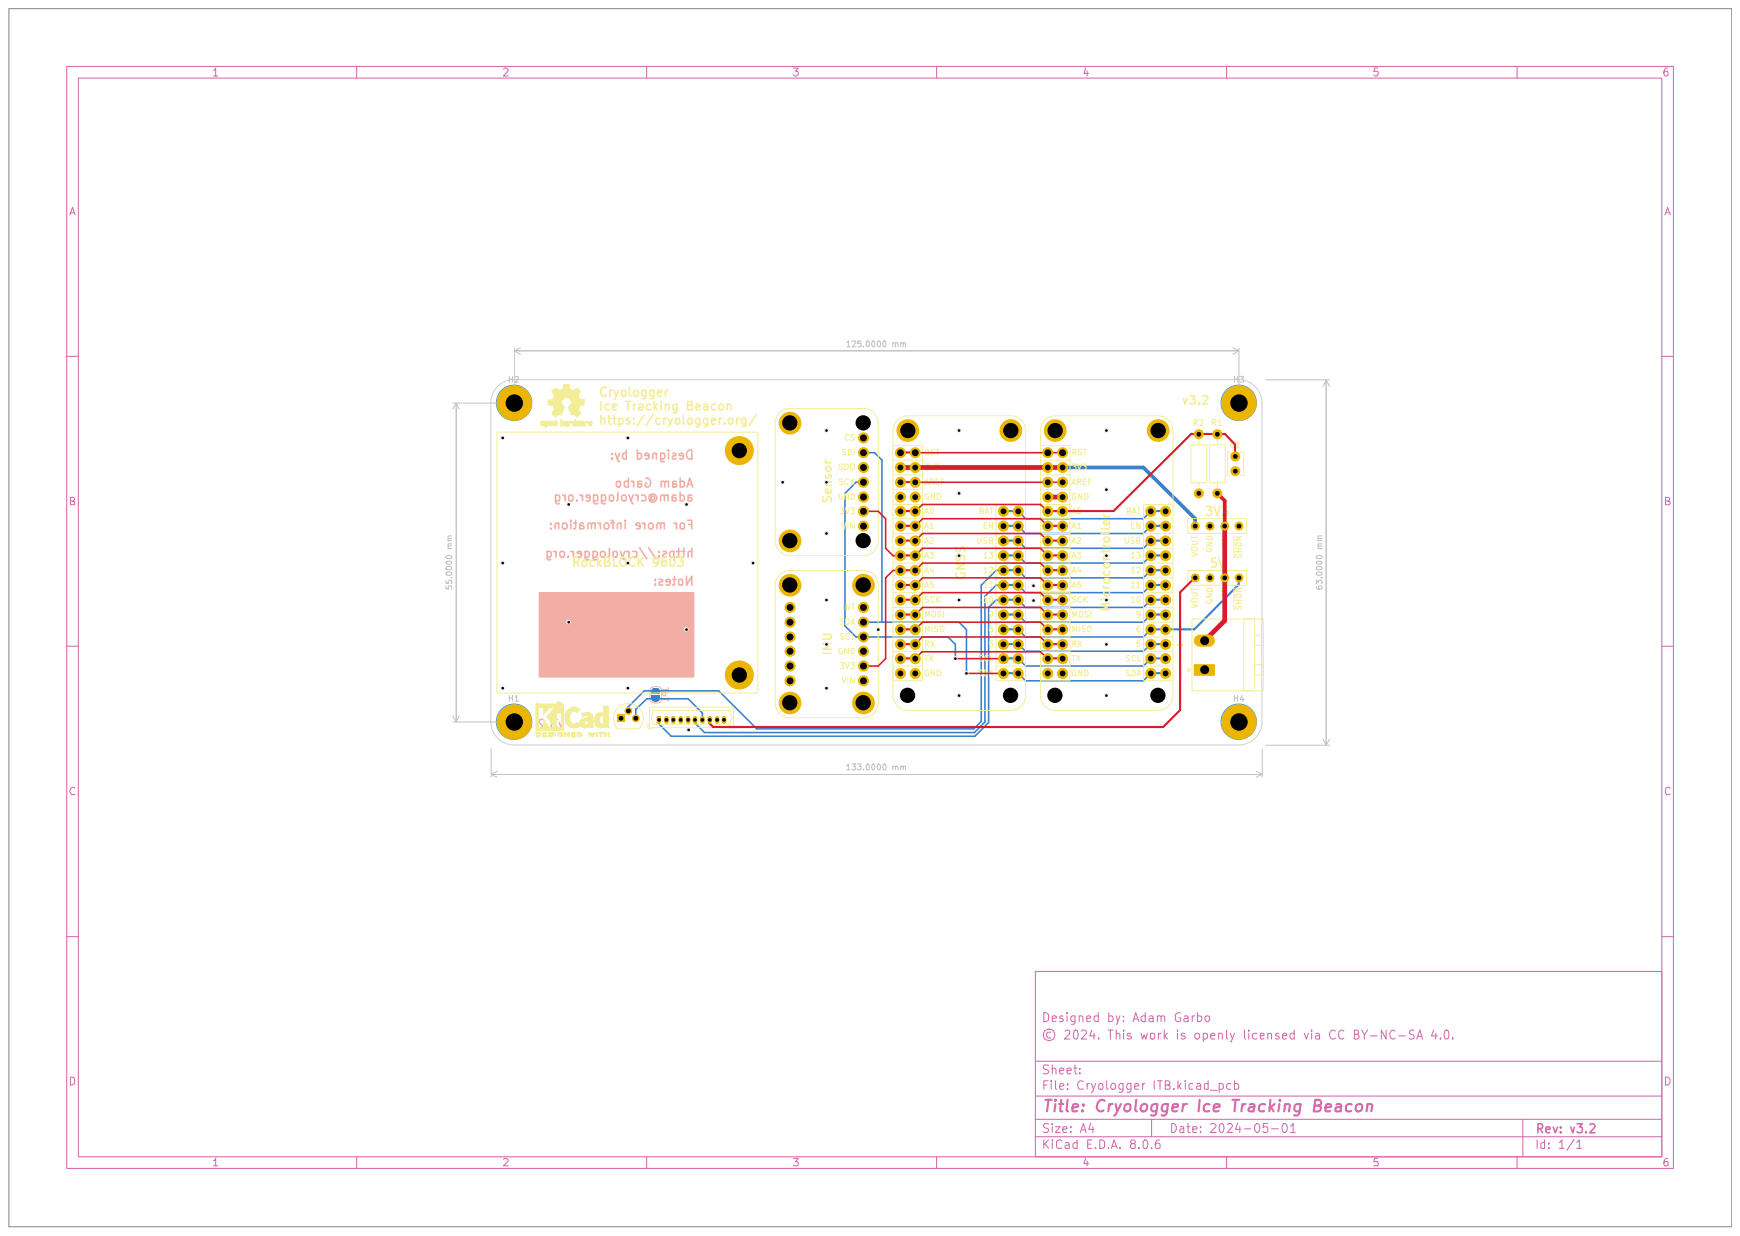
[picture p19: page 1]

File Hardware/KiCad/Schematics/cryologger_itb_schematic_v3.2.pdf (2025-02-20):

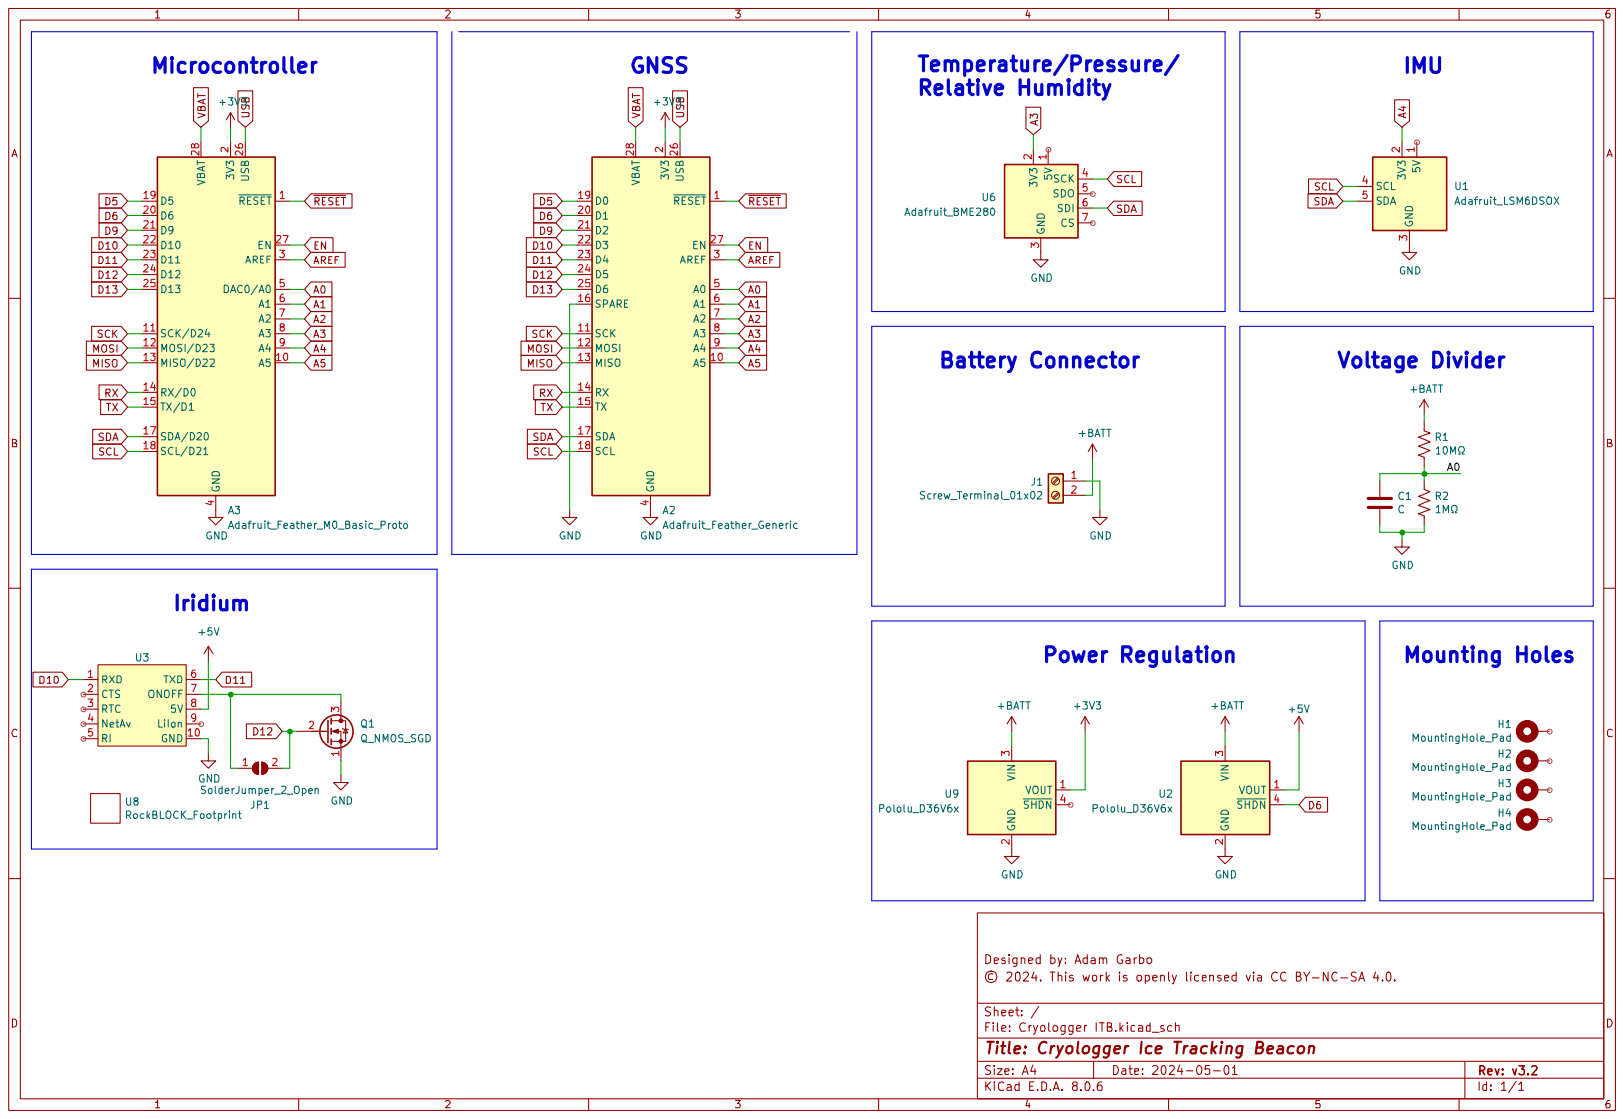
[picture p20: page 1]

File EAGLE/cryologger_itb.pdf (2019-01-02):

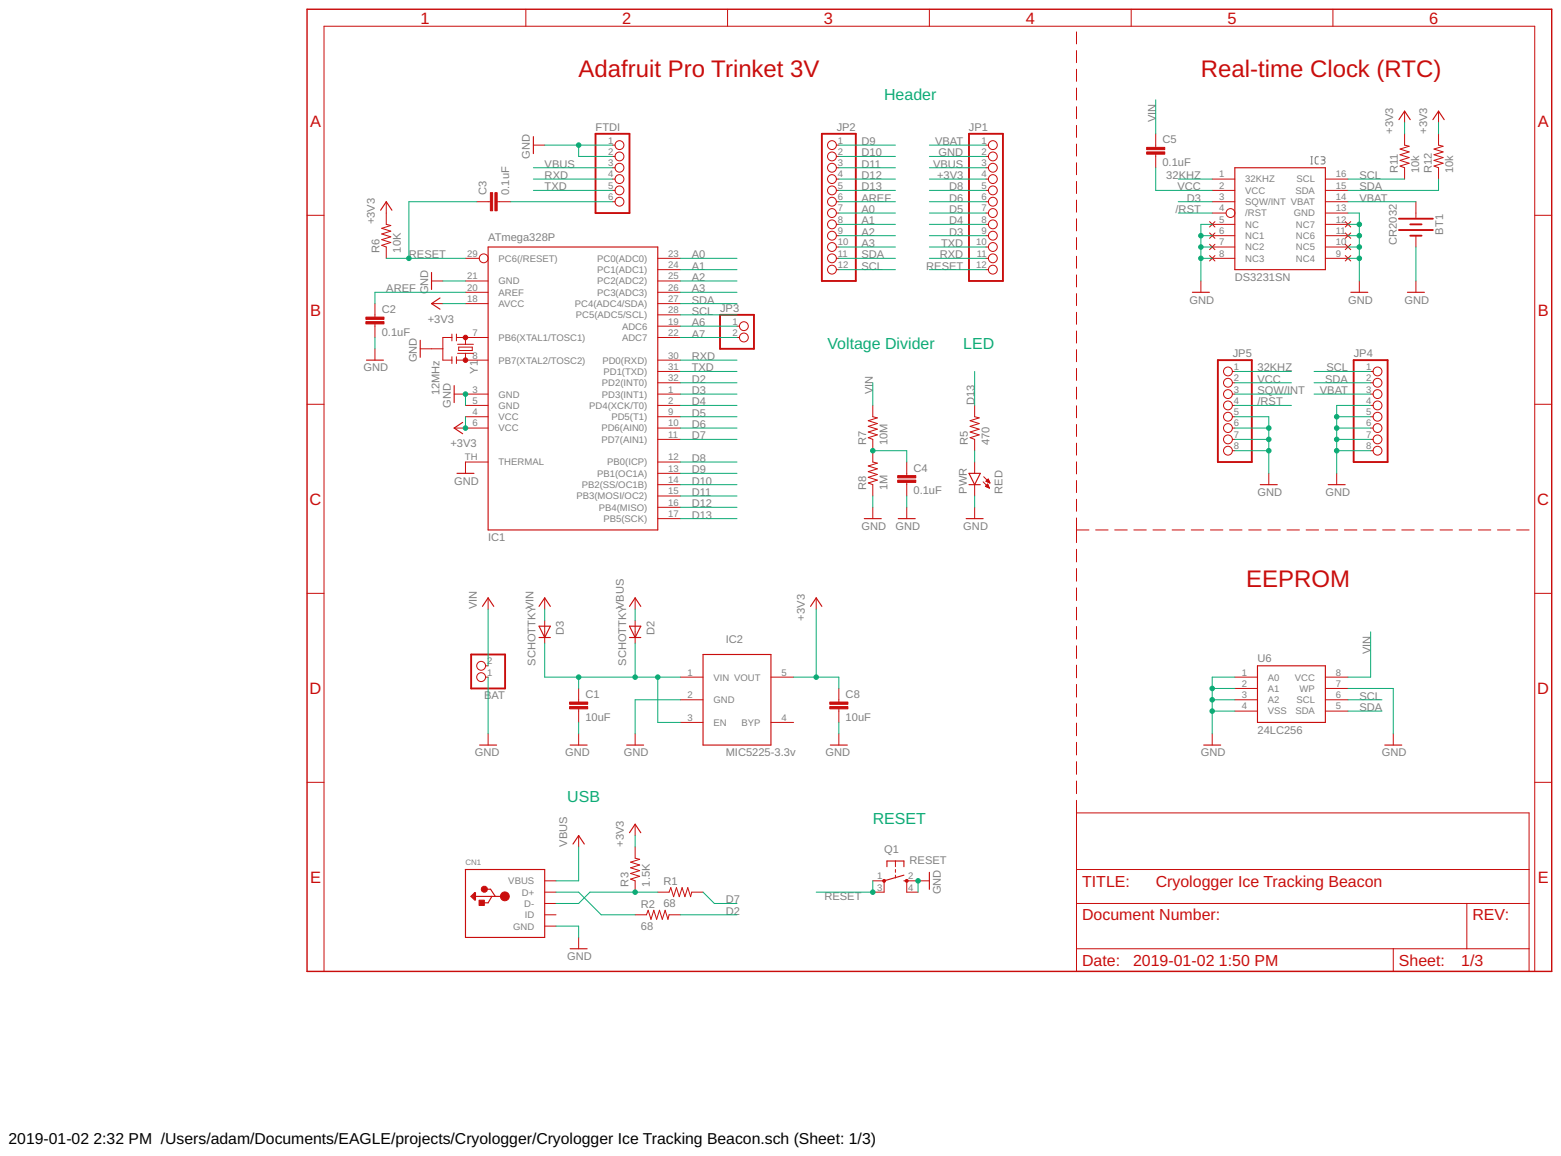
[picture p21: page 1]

Cryologger Ice Tracking Beacon

Document Number: | REV:

Date: 2019-01-02 1:50 PM | Sheet: 1/3

2019-01-02 2:32 PM /Users/adam/Documents/EAGLE/projects/Cryologger/Cryologger Ice Tracking Beacon.sch (Sheet: 1/3)

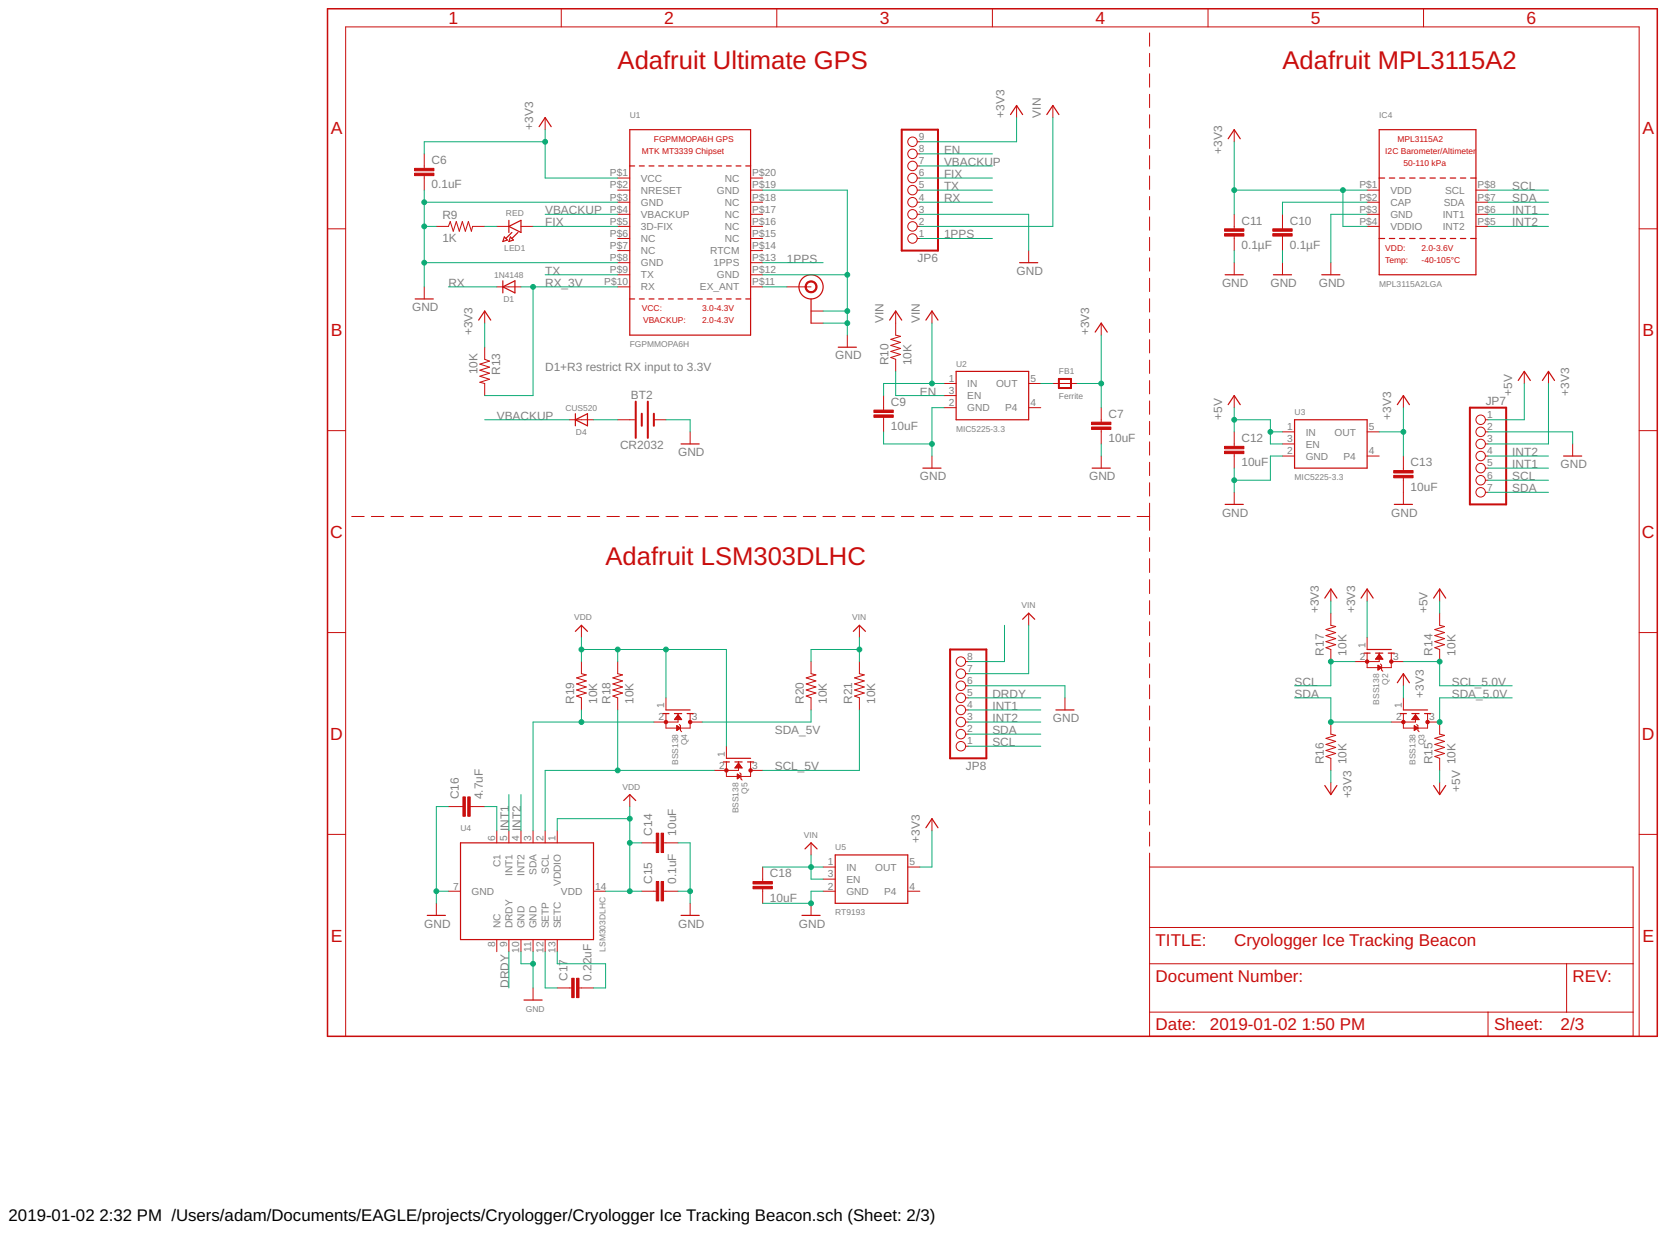
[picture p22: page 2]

D1+R3 restrict RX input to 3.3V

Cryologger Ice Tracking Beacon

Document Number: | REV:

Date: 2019-01-02 1:50 PM | Sheet: 2/3

2019-01-02 2:32 PM /Users/adam/Documents/EAGLE/projects/Cryologger/Cryologger Ice Tracking Beacon.sch (Sheet: 2/3)

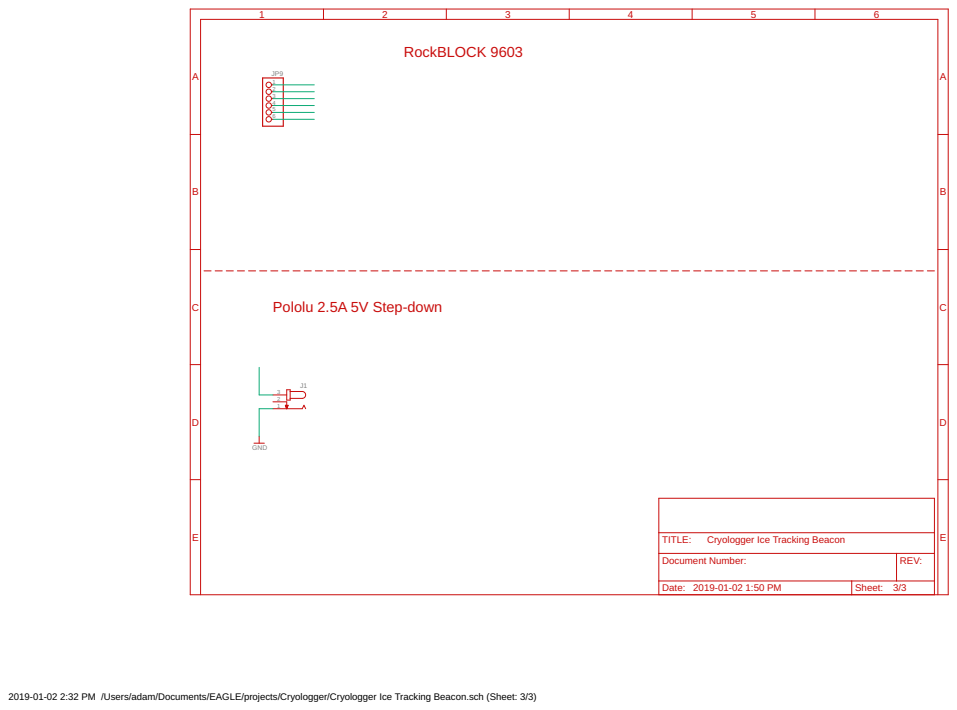
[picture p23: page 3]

Cryologger Ice Tracking Beacon

Document Number: | REV:

Date: 2019-01-02 1:50 PM | Sheet: 3/3

2019-01-02 2:32 PM /Users/adam/Documents/EAGLE/projects/Cryologger/Cryologger Ice Tracking Beacon.sch (Sheet: 3/3)

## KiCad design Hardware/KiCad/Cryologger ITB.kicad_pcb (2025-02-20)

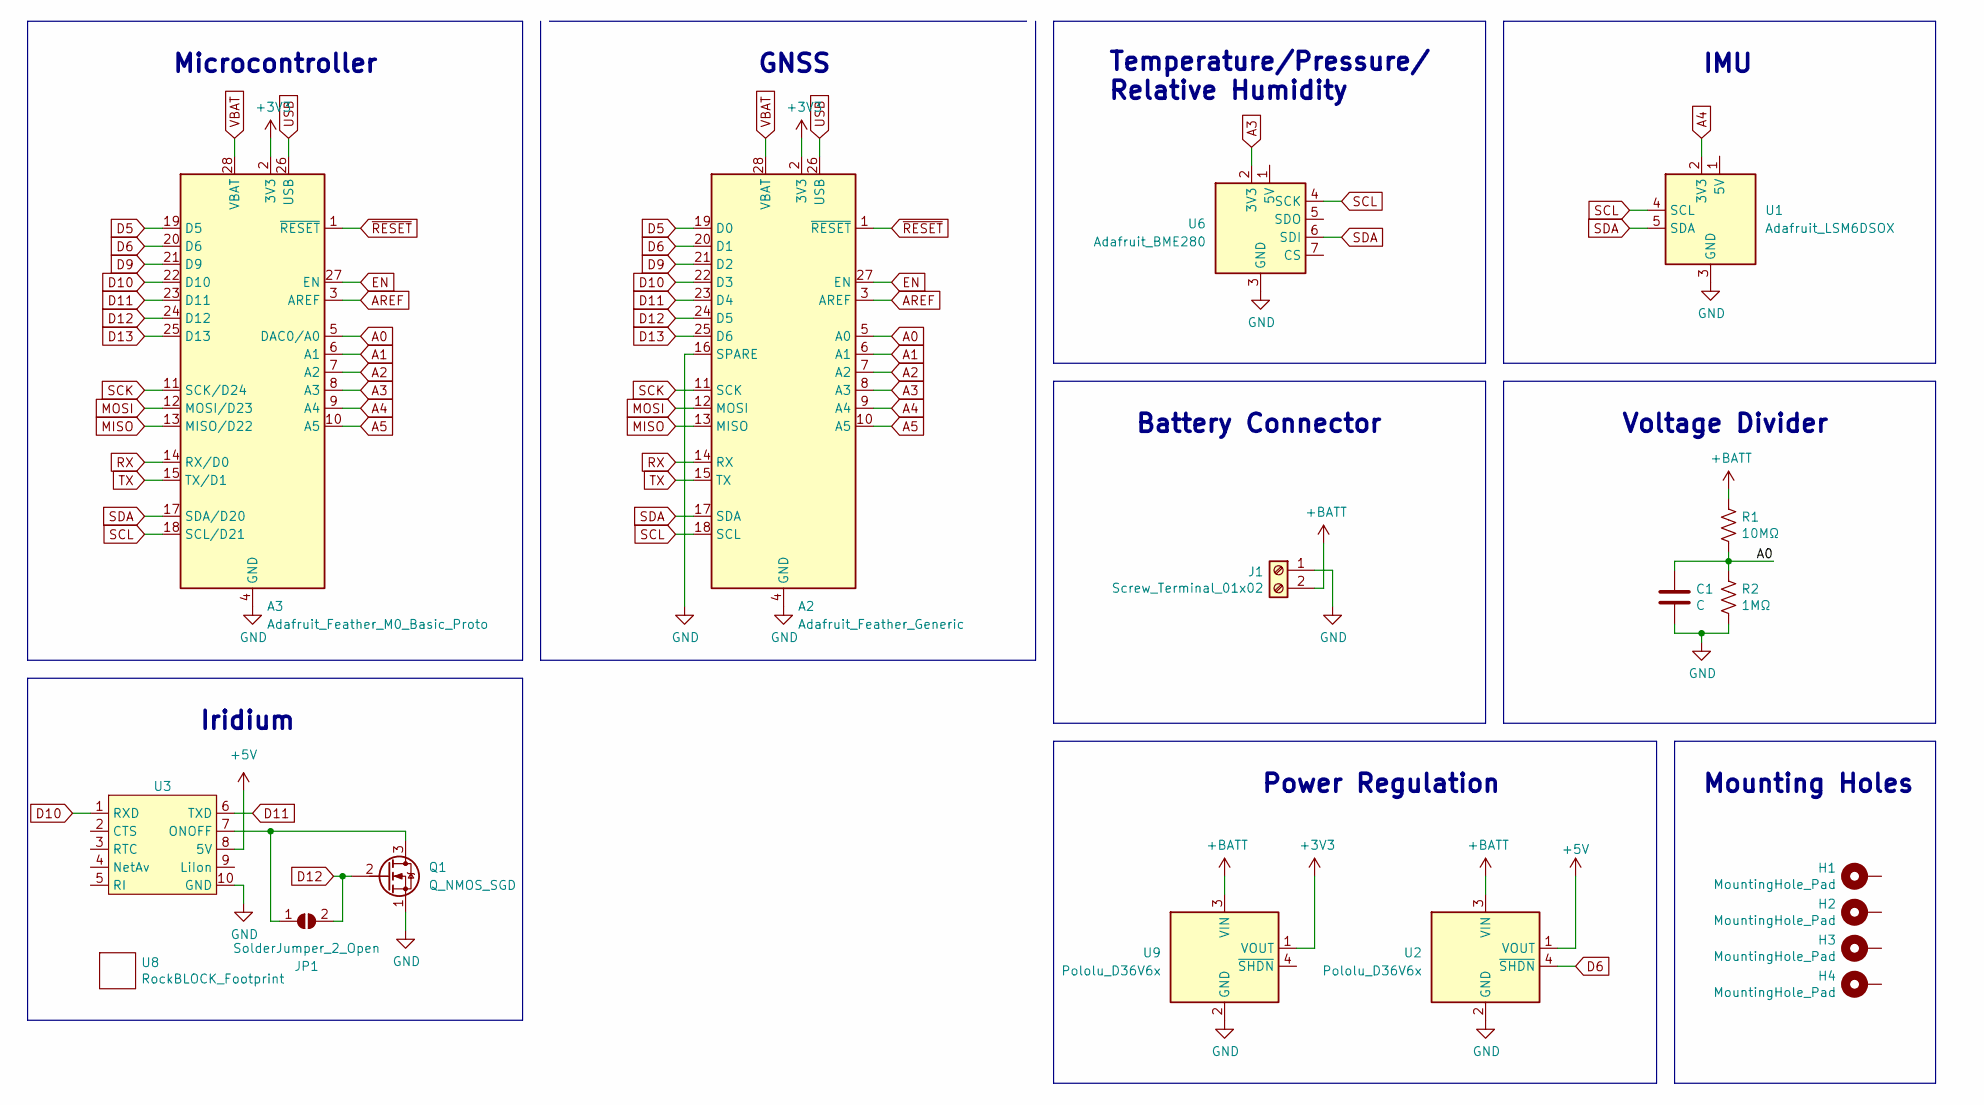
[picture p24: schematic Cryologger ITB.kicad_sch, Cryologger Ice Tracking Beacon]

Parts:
A2: Adafruit_Feather_Generic; Adafruit_Feather_Header_Double
A3: Adafruit_Feather_M0_Basic_Proto; Adafruit_Feather_Header_Double
C1: C; C_Disc_D3.8mm_W2.6mm_P2.50mm
H1, H2, H3, H4: MountingHole_Pad; MountingHole_3mm_Pad
J1: Screw_Terminal_01x02; PhoenixContact_MSTBA_2,5_2-G-5,08_1x02_P5.08mm_Horizontal
JP1: SolderJumper_2_Open; SolderJumper-2_P1.3mm_Open_RoundedPad1.0x1.5mm
Q1: Q_NMOS_SGD; TO-92
R1: 10MΩ; R_Axial_DIN0207_L6.3mm_D2.5mm_P10.16mm_Horizontal
R2: 1MΩ; R_Axial_DIN0207_L6.3mm_D2.5mm_P10.16mm_Horizontal
U1: Adafruit_LSM6DSOX; Adafruit_LSM6DS0X
U2, U9: Pololu_D36V6x
U3: Molex_PicoBlade_53047-1010_1x10_P1.25mm_Vertical
U6: Adafruit_BME280
U8: RockBLOCK_Footprint; RockBLOCK_9603

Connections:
+3V3: A2.2 (3V3), A3.2 (3V3), U9.1 (VOUT)
+5V: U2.1 (VOUT), U3.8 (5V)
+BATT: J1.2, R1.1, U2.3 (VIN), U9.3 (VIN)
A0: A2.5 (A0), A3.5 (DAC0/A0), C1.1, R1.2, R2.1
A1: A2.6 (A1), A3.6 (A1)
A2: A2.7 (A2), A3.7 (A2)
A3: A2.8 (A3), A3.8 (A3), U6.2 (3V3)
A4: A2.9 (A4), A3.9 (A4), U1.2 (3V3)
A5: A2.10 (A5), A3.10 (A5)
AREF: A2.3 (AREF), A3.3 (AREF)
D5: A2.19 (D0), A3.19 (D5)
D6: A2.20 (D1), A3.20 (D6), U2.4 (~SHDN)
D9: A2.21 (D2), A3.21 (D9)
D10: A2.22 (D3), A3.22 (D10), U3.1 (RXD)
D11: A2.23 (D4), A3.23 (D11), U3.6 (TXD)
D12: A2.24 (D5), A3.24 (D12), JP1.2 (B), Q1.2 (G)
D13: A2.25 (D6), A3.25 (D13)
EN: A2.27 (EN), A3.27 (EN)
GND: A2.4 (GND), A2.16 (SPARE), A3.4 (GND), A3.16 (GND), C1.2, J1.1, Q1.1 (S), R2.2, U1.3 (GND), U2.2 (GND), U3.10 (GND), U6.3 (GND), U9.2 (GND)
MISO: A2.13 (MISO), A3.13 (MISO/D22)
MOSI: A2.12 (MOSI), A3.12 (MOSI/D23)
unnamed: JP1.1 (A), Q1.3 (D), U3.7 (ONOFF)
RX: A2.14 (RX), A3.14 (RX/D0)
SCK: A2.11 (SCK), A3.11 (SCK/D24)
SCL: A2.18 (SCL), A3.18 (SCL/D21), U1.4 (SCL), U6.4 (SCK)
SDA: A2.17 (SDA), A3.17 (SDA/D20), U1.5 (SDA), U6.6 (SDI)
TX: A2.15 (TX), A3.15 (TX/D1)
USB: A2.26 (USB), A3.26 (USB)
VBAT: A2.28 (VBAT), A3.28 (VBAT)
~RESET: A2.1 (~RESET), A3.1 (~RESET)

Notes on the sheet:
Microcontroller
Power Regulation
Iridium
Mounting Holes
Battery Connector
IMU
Voltage Divider
Temperature/Pressure/ Relative Humidity
GNSS

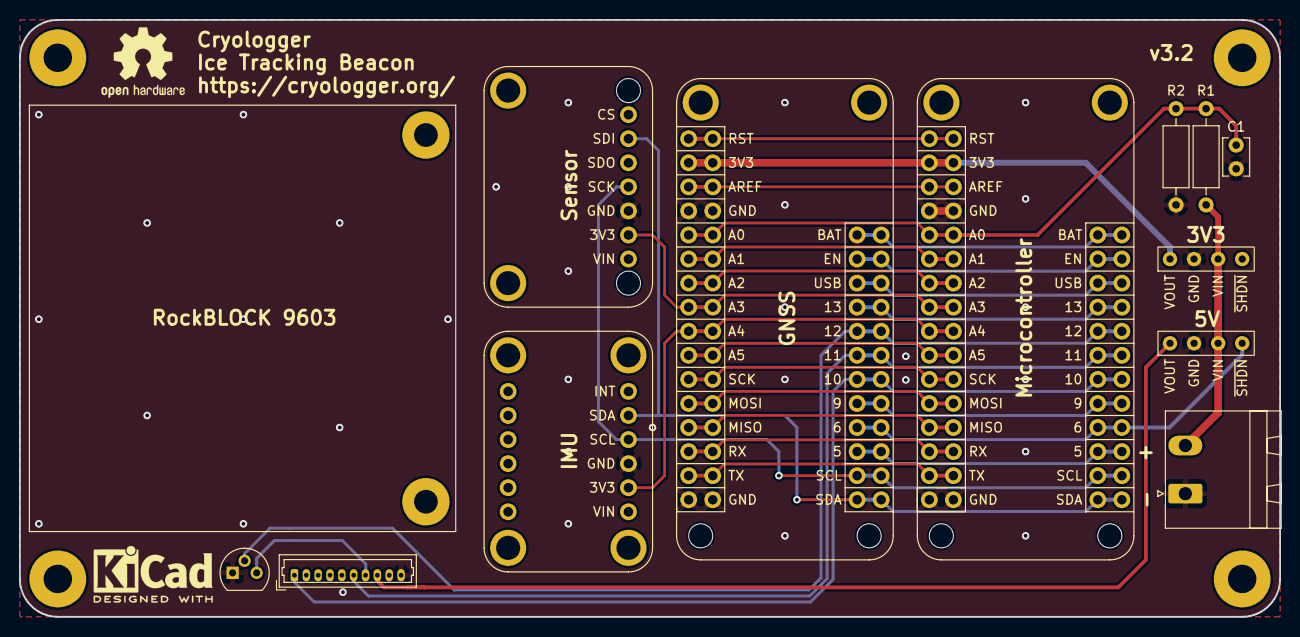
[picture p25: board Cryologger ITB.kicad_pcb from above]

Board: 2 copper layers, 133.0 x 63.0 mm, 18 parts (1 on the bottom side), 30 nets.

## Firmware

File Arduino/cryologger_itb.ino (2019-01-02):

/*
  Title:          Cryologger Ice Tracking Beacon (ITB)
  Author:         Adam Garbo
  Last modified:  August 25, 2018
  Description:    Ice tracking beacon intended for deployment in the Canadian Arctic.
*/

// Libraries
#include <avr/interrupt.h>      // https://www.nongnu.org/avr-libc/user-manual/group__avr__interrupts.html
#include <avr/power.h>          // https://www.nongnu.org/avr-libc/user-manual/group__avr__power.html
#include <avr/sleep.h>          // https://www.nongnu.org/avr-libc/user-manual/group__avr__sleep.html
#include <avr/wdt.h>            // https://www.nongnu.org/avr-libc/user-manual/group__avr__watchdog.html
#include <DS3232RTC.h>          // https://github.com/JChristensen/DS3232RTC
#include <extEEPROM.h>          // https://github.com/JChristensen/extEEPROM
#include <IridiumSBD.h>         // https://github.com/mikalhart/IridiumSBD
#include <LSM303.h>             // https://github.com/pololu/lsm303-arduino
#include <SoftwareSerial.h>     // https://www.arduino.cc/en/Reference/SoftwareSerial (included with Arduino IDE)
#include <SparkFunMPL3115A2.h>  // https://github.com/sparkfun/MPL3115A2_Breakout/
#include <TinyGPS.h>            // https://github.com/mikalhart/TinyGPS
#include <Wire.h>               // https://www.arduino.cc/en/Reference/Wire (included with Arduino IDE)

// Defined constants
#define DEBUG                   // Echo data to serial port. Comment line to prevent all Serial.print() commands
#define LED               13    // LED activity and error indicator
#define RTC_ALARM_PIN     3     // Connect DS3231 SQW/INT to Pro Trinket D3 pin (INT1)
#define GPS_RX            4     // Connect GPS Rx to Pro Trinket D4 pin
#define GPS_TX            5     // Connect GPS Tx to Pro Trinket D5 pin
#define GPS_EN            6     // Connect GPS EN to Pro Trinket D6 pin
#define ROCKBLOCK_EN      8     // Connect Pololu step-down voltage regulator EN to Pro Trinket D8 pin
#define ROCKBLOCK_SLEEP   9     // Connect RockBLOCK Sleep to Pro Trinket D9 pin
#define ROCKBLOCK_TX      10    // Connect RockBLOCK Tx to Pro Trinket D10 pin
#define ROCKBLOCK_RX      11    // Connect RockBLOCK Rx to Pro Trinket D11 pin

// Software serial ports
SoftwareSerial    ssGps(GPS_TX, GPS_RX);
SoftwareSerial    ssIridium(ROCKBLOCK_RX, ROCKBLOCK_TX);

// Object instantiations
extEEPROM       extEeprom(kbits_512, 1, 128, 0x50);
IridiumSBD      isbd(ssIridium, ROCKBLOCK_SLEEP);
LSM303          lsm303;
MPL3115A2       mpl3115a2;
time_t          t, alarmTime;
tmElements_t    tm;
TinyGPS         tinyGps;

// User defined global variable declarations
unsigned long   alarmInterval           = 3600;    // Sleep duration (in seconds) between data sample acquisitions
unsigned int    transmitInterval        = 1;      // Number of data samples to be included in a single transmission (340 byte limit)
unsigned int    maxRetransmitCounter    = 9;      // Maximum number of failed data transmissions to reattempt in a single message (340 byte limit)

// Global variable declarations
const unsigned int    maxEepromAddress        = 30000;    // Maximum writeable address of external EEPROM
volatile bool         alarmIsrWasCalled       = false;    // DS3231 RTC alarm interrupt service routine (ISR) flag
volatile bool         wdtIsrWasCalled         = true;     // Watchdog Timer (WDR) ISR flag
volatile bool         sleeping                = true;     // Sleep flag for WDT ISR
unsigned int          retransmitCounter       = 0;        // RockBLOCK failed data transmission counter
unsigned int          currentEepromAddress    = 0;        // Initial external EEPROM write location
unsigned int          transmitCounter         = 0;        // RockBLOCK data transmission counter
unsigned int          messageCounter          = 0;        // Global RockBLOCK data transmission counter
unsigned int          transmitDuration        = 0;        // Global RockBLOCK data transmission time variable
unsigned long         previousMillis          = 0;        // Global RockBLOCK callback function timer variable

// Union
typedef union
{
  struct
  {
    unsigned long   unixtime;           // (4 bytes)  Date and time in time_t format (seconds since epoch)
    //int             tempDs3231;         // (2 bytes)  DS3231 RTC internal temperature (°C)
    int             temperature;        // (2 bytes)  MPL3115A2 temperature (°C)
    unsigned int    pressure;           // (2 bytes)  MPL3115A2 pressure (Pa)
    int             pitch;              // (2 bytes)  LSM303 pitch (°)
    int             roll;               // (2 bytes)  LSM303 roll (°)
    unsigned int    heading;            // (2 bytes)  LSM303 tilt-compensated heading (°)
    long            latitude;           // (4 bytes)  GPS latitude (DD)
    long            longitude;          // (4 bytes)  GPS longitude (DD)
    unsigned int    satellites;         // (2 bytes)  GPS number of satellites
    unsigned int    hdop;               // (2 bytes)  GPS HDOP
    unsigned int    voltage;            // (2 bytes)  Battery voltage (mV)
    unsigned int    transmitDuration;   // (2 bytes)  Data transmission time (seconds)
    unsigned int    messageCounter;   // (2 bytes)  Data transmission counter

  } __attribute__((packed));            // 30 bytes total
  byte bytes[];
} SBDMessage;

SBDMessage message;
size_t messageSize = sizeof(message); // Size (in bytes) of data to be stored and transmitted

// Setup
void setup()
{
#ifdef DEBUG
  Serial.begin(115200);
#endif // DEBUG

  Wire.begin();   // Enable SDA & SCL internal pull-up resistors

  // Configure digital pins
  pinMode(LED, OUTPUT);               // LED pin
  pinMode(GPS_EN, OUTPUT);            // GPS EN (enable) pin
  pinMode(ROCKBLOCK_EN, OUTPUT);      // Step-down voltage regulator EN (enable) pin
  digitalWrite(GPS_EN, LOW);          // Set GPS EN pin LOW (0 V) to disable onboard regulator
  digitalWrite(ROCKBLOCK_EN, LOW);    // Set step-down EN pin LOW (0 V) to disable step-down voltage regulator

  // Configure the Watchdog Timer
  configureWatchdog();

  // External EEPROM
  byte i2cStat = extEeprom.begin(extEEPROM::twiClock400kHz);
  if (i2cStat != 0)
  {
#ifdef DEBUG
    Serial.println(F("Unable to initialize EEPROM!"));
#endif // DEBUG
  }

  // Configure RockBLOCK
  isbd.attachConsole(Serial);       // Monitor serial traffic to/from the RockBLOCK
  isbd.attachDiags(Serial);         // Diagnostic routine to monitor debug messages
  isbd.setPowerProfile(0);          // Defines the internal delays between retransmission (0 = direct connect (default), 1 = USB)
  isbd.useMSSTMWorkaround(false);   // Disable “MSSTM” software query workaround

  // DS3231 Real-time clock (RTC)
  RTC.setAlarm(ALM1_MATCH_DATE, 0, 0, 0, 1);    // Initialize alarm 1 to known value
  RTC.setAlarm(ALM2_MATCH_DATE, 0, 0, 0, 1);    // Initialize alarm 2 to known value
  RTC.alarm(ALARM_1);                           // Clear alarm 1 interrupt flag
  RTC.alarm(ALARM_2);                           // Clear alarm 2 interrupt flag
  RTC.alarmInterrupt(ALARM_1, false);           // Disable interrupt output for alarm 1
  RTC.alarmInterrupt(ALARM_2, false);           // Disable interrupt output for alarm 2
  RTC.squareWave(SQWAVE_NONE);                  // Configure INT/SQW pin for interrupt operation by disabling default square wave output

  /*
    // Set RTC to an arbitrary time (for debugging purposes)
    tm.Hour = 10;
    tm.Minute = 59;
    tm.Second = 55;
    tm.Day = 26;
    tm.Month = 7;
    tm.Year = 2018 - 1970;    // tmElements_t.Year is the offset from 1970
    time_t t = makeTime(tm);  // change the tm structure into time_t (seconds since epoch)
    RTC.set(t);
  */

#ifdef DEBUG
  Serial.print(F("Cryologger #6 "));
  printDateTime(RTC.get());   // Display current date and time
#endif // DEBUG

  pinMode(RTC_ALARM_PIN, INPUT_PULLUP);       // Enable internal pull-up resistor on Pro Trinket external interrupt pin D3
  attachInterrupt(INT1, alarmIsr, FALLING);   // Wake on falling edge of RTC_ALARM_PIN

  // Set alarm 1
  //RTC.setAlarm(ALM1_MATCH_SECONDS, 0, 0, 0, 1);     // Set initial alarm to occur at seconds rollover
  RTC.setAlarm(ALM1_MATCH_MINUTES, 0, 0, 0, 1);     // Set initial alarm to occur at minutes rollover
  RTC.alarm(ALARM_1);                               // Ensure alarm 1 interrupt flag is cleared
  RTC.alarmInterrupt(ALARM_1, true);                // Enable interrupt output for alarm 1
}

// Loop
void loop()
{
  if ((alarmIsrWasCalled) || (wdtIsrWasCalled))
  {
    t = RTC.get();            // Read current date and time from RTC
    if (RTC.alarm(ALARM_1))   // Check alarm 1 and clear flag if set
    {
#ifdef DEBUG
      Serial.println(F("===================================="));
      Serial.print(F("Cryologger #6 Alarm: ")); printDateTime(t);
      Serial.println(F("===================================="));
#endif // DEBUG

      transmitCounter++;    // Increment data transmission interval counter
      messageCounter++;     // Increment data transmission counter (provides indication of system reset)
      message.messageCounter = messageCounter;  // Write iteration counter value to union

#ifdef DEBUG
      Serial.print(F("transmitCounter: ")); Serial.println(transmitCounter);
      Serial.print(F("messageCounter: ")); Serial.println(messageCounter);
#endif // DEBUG

      // Read sensors
      readBattery();    // Read battery voltage (mV) from voltage divider
      readDs3231();     // Read date and time from RTC
      readMpl3115a2();  // Read temperature (°C) and pressure (Pa) from MPL3115A2 sensor
      readGps();        // Read latitude and longitude (DD), number of satellites, and HDOP from GPS
      readLsm303();     // Read pitch, roll and tilt-compensated heading from LSM303 sensor (°)
      writeEeprom();    // Write data stored in union to external EEPROM

      // Data transmission check
      if (transmitCounter == transmitInterval)
      {
        transmitData();
        transmitCounter = 0;
      }
#ifdef DEBUG
      Serial.print(F("transmitCounter: ")); Serial.println(transmitCounter);
#endif // DEBUG

      // Set alarm 1
      alarmTime = t + alarmInterval;    // Calculate next alarm
      RTC.setAlarm(ALM1_MATCH_DATE, second(alarmTime), minute(alarmTime), hour(alarmTime), day(alarmTime));   // Set alarm
      RTC.alarm(ALARM_1);               // Ensure alarm 1 interrupt flag is cleared

      // Check if alarm was set in the past
      if (RTC.get() >= alarmTime)
      {
#ifdef DEBUG
        Serial.println(F("*** Warning! Alarm set in the past ***"));
        Serial.print(F("Previous alarm: ")); printDateTime(alarmTime);
#endif // DEBUG
        t = RTC.get();                    // Read current date and time from RTC
        alarmTime = t + alarmInterval;    // Calculate next alarm
        RTC.setAlarm(ALM1_MATCH_DATE, second(alarmTime), minute(alarmTime), hour(alarmTime), day(alarmTime));
        RTC.alarm(ALARM_1);               // Ensure alarm 1 interrupt flag is cleared
      }
#ifdef DEBUG
      Serial.print(F("Current time: ")); printDateTime(RTC.get());
      Serial.print(F("New alarm: ")); printDateTime(alarmTime);
#endif // DEBUG
    }
    blink(1, 5);                // Watchdog Timer visual indicator
    alarmIsrWasCalled = false;  // Reset RTC ISR flag
    wdtIsrWasCalled = false;    // Reset WDT ISR flag
    goToSleep();                // Sleep
  }
}

// Functions
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

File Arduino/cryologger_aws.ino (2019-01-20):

/*
    Title:          Cryologger - Automatic Weather Station (AWS)
    Last modified:  January 20, 2019
    Author:         Adam Garbo

    Components:
    - Adafruit Feather M0 Adalogger
    - Adafruit DS3231 RTC Precision Featherwing
    - Davis Instruments 7911 Anemomenter
    - Davis Instruments 7817 Thermistor
    - Rock Seven RockBLOCK 9603
    - Pololu 3.3V, 600mA Step-Down Voltage Regulator D36V6F3
    - 256 MB microSD card (industrial rated)
*/

#include <Arduino.h>            // https://github.com/arduino/ArduinoCore-samd (Required before wiring_private.h)
#include <ArduinoLowPower.h>    // https://github.com/arduino-libraries/ArduinoLowPower
#include <DS3232RTC.h>          // https://github.com/JChristensen/DS3232RTC
#include <IridiumSBD.h>         // https://github.com/mikalhart/IridiumSBD
#include <math.h>               // https://www.nongnu.org/avr-libc/user-manual/group__avr__math.html
#include <Statistic.h>          // https://github.com/RobTillaart/Arduino/tree/master/libraries/Statistic
#include <SdFat.h>              // https://github.com/greiman/SdFat
#include <SparkFunBME280.h>     // https://github.com/sparkfun/SparkFun_BME280_Arduino_Library
#include <SPI.h>                // https://www.arduino.cc/en/Reference/SPI
#include <Wire.h>               // https://www.arduino.cc/en/Reference/Wire
#include <wiring_private.h>     // pinPeripheral() function

// Required for Serial when selecting a board type other than Adafruit Feather M0
#if defined(ARDUINO_SAMD_ZERO) && defined(SERIAL_PORT_USBVIRTUAL)
#define Serial SERIAL_PORT_USBVIRTUAL
#endif

// Defined constants
#define GPIO_PWR_PIN              A3
#define LED_PIN                   8
#define RTC_INT_PIN               5
#define ROCKBLOCK_EN_PIN          6
#define ROCKBLOCK_SLEEP_PIN       12
#define ROCKBLOCK_RX_PIN          11
#define ROCKBLOCK_TX_PIN          10
#define THERMISTOR_PIN            A4
#define WIND_SPEED_PIN            A1
#define WIND_DIRECTION_PIN        A2
#define VBAT_PIN                  A0

#define DEBUG   false

// Create a new Serial instance. For more information see: https://www.arduino.cc/en/Tutorial/SamdSercom
Uart Serial2 (&sercom1, ROCKBLOCK_RX_PIN, ROCKBLOCK_TX_PIN, SERCOM_RX_PAD_0, UART_TX_PAD_2);  // Create the new UART instance assigning it to pin 10 and 11
#define IridiumSerial Serial2

// Attach the interrupt handler to the SERCOM
void SERCOM1_Handler()
{
  Serial2.IrqHandler();
}

// Object instantiations
BME280        mySensor;
DS3232RTC     myRTC(false);     // Tell constructor not to initialize the I2C bus
IridiumSBD    modem(IridiumSerial, ROCKBLOCK_SLEEP_PIN);
SdFat         sd;               // File system object
SdFile        file;             // Log file
time_t        t, unixtime, alarmTime;
tmElements_t  tm;

// Statistic objects
Statistic batteryStats;           // Battery voltage statistics
Statistic temperatureIntStats;    // BME280 internal temperature statistics
Statistic humidityStats;          // BME280 internal humidity statistics
Statistic pressureStats;          // BME280 internal pressure statistics
Statistic temperatureExtStats;    // Davis 7817 thermistor external temperature statistics
Statistic windSpeedStats;         // Anemometer wind speed statistics
Statistic vnStats;                // Anemoeter north-south wind vector component (v) statistics
Statistic veStats;                // Anemometer east-west wind vector component (u) statistics
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

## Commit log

2019-09-23 Inital Cryologger V2 update
    [cryologger_itb.sch, cryologger_itb_bom.csv]
2019-10-08 Cryologger V2 update
    [Cryologger V2 - Bill of Materials.csv]
2020-03-18 Cryologger V3 update
    [cryologger_itb_v1.csv, cryologger_itb_v1.sch, cryologger_itb_v2.csv]
2020-11-02 Standardize project folders
    [cryologger_itb_v1.sch]
2020-11-17 Update Qwiic Micro code
    Add support for WS2812B RGB LED (aka NeoPixel) and ICM-20948 IMU
2020-12-23 Update v1.0 documentation
    Standardize folder naming structure. Add deployment and tracjectory maps. Add photos of icebergs and beacon deployments.
    [cryologger_itb_v1.csv, cryologger_itb_v1.sch, cryologger_itb_v2.csv]
2020-12-27 Remove unsupported WS2812B LED code from MicroMod
2020-12-29 Major update to Qwiic Micro code
    Add external RTC code. Switch to debug print macros. Remove all code relating to SparkX products (i.e. Qwiic Power Switch, Qwiic Iridium 9603N).
2020-12-31 Add MOSFET to Qwiic Micro to control power to peripherals
    Improve RTC alarms. Improve non-blocking blink delays. Improve power down and power up flow.
2021-01-01 Change method of printing MT-SBD message
2021-01-02 Configuration for prototype testing
2021-01-04 Minor updates for prototype testing
2021-01-07 MicroMod prototype testing changes
2021-01-09 Add delay to sensor readings
2021-01-15 MicroMod prototype code updates
2021-04-14 Add power control functions
2021-04-16 Update low power test code
2021-04-22 Major update
    Feed RTC-configured GCLK2 to WDT. Rework processing of MT-SBD messages. Standardize SBD variable names. Rework functions to print MO/MT-SBD messages. Revert to iterationCounter variable name.
2021-05-12 Remove RGB LED code
2021-05-25 Switch to DPS310 temperature/pressure sensor
2021-05-25 Prototype testing modifications
2021-05-25 Update analog pin for battery measurements
2021-06-02 Add KiCad files
    [Cryologger ITB-B_Cu.gbl, Cryologger ITB-B_Mask.gbs, Cryologger ITB-B_Paste.gbp, Cryologger ITB-B_SilkS.gbo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]
2021-06-16 Remove prototype code
2021-07-27 Add IMU calibration data
2021-07-28 Add missing IMU calibration data
2021-08-01 Add 3D-printed mounting STL files
    [battery_mount_left.stl, battery_mount_right.stl, battery_mount_top.stl, pcb_mount_left.stl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]
2022-04-14 Update bill of materials
2022-06-01 Update battery voltage measurement to 10/1 MOhm resistor divider
    Make two measurements to ensure correct reading.
2022-06-01 Add testing code for voltage divider battery measurements
2022-10-20 Merge IMU with sensors tab
    Add code support for BME280 and LSM303AGR sensors. Rename functions to be specific to the sensor.
2022-10-20 Add ADC calibration and float mapping functionality
2022-10-22 Minor updates
    Updated function names and specified which LED for blink function.
2022-10-22 Add LSM303AGR min/max calibration code
2022-10-22 Change voltage divider calculation
    Standardized code with Cryologger AWS repository.
2022-12-04 Minor updates
    Updated code to LMS303AGR accelerometer/magnetometer. Improved program flow.
2023-01-22 Remove DPS310 code and rename alarmInterval to sampleInterval
    Continued work on standardizing AWS and ITB code (i.e., functions, logic, etc.). Added battery voltage cutoff alarm. Changed sample interval to minutes.
2023-01-22 Standardize loop program logic
    Moved transmission logic to main loop. Added sample counter.
2023-03-05 Major changes to KiCad design files
    Updated design to v3.1. Began standardization of Cryologger designs to metric measurements. Redid schematic using Cryologger library symbols and footprints. Generated new Gerber design files. Generat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
    [Cryologger ITB-B_Cu.gbl, Cryologger ITB-B_Mask.gbs, Cryologger ITB-B_Paste.gbp, Cryologger ITB-B_SilkS.gbo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]
2023-03-05 Reorganized software files
    Created new Arduino folder to store firmware and test code.
2023-04-04 Add 3D printing files for case
    [case_v3.1.stl, cover_v3.1.stl]
2023-04-04 Add 3D printing G-Code
2023-04-04 Minor updates to PCB design
    [Cryologger ITB.kicad_pcb]
2023-04-16 Minor updates
    Fixed location of sleep code. Rearranged order of when sensors are powered up. Converted library links to open Arduino IDE Library Manager.
2023-04-17 Print correct RTC alarm
2023-04-17 Create Cryologger ITB.step
    [Cryologger ITB.step]
2023-06-28 Update SAMD board definition version
2023-07-04 Standardize size of sampleInterval in struct/union
2023-09-04 Revert documentation to legacy Arduino IDE
2023-10-21 Fix maximum sample interval
2023-10-21 Update version
    Removed magnetometer calibration deployment values.
2024-03-14 Add N-MOSFET and to control on/off logic of RockBLOCK v3.F
    Added a jumper to ensure N-MOSFET is backwards compatible. Updated files to KiCad 8.0.
    [Cryologger ITB.kicad_pcb, Cryologger ITB.kicad_sch]
2024-05-03 Add N-MOSFET to PCB to control RockBLOCK v3.F
    Updated KiCad files. Added Creative Commons license.
    [Cryologger ITB-B_Cu.gbl, Cryologger ITB-B_Mask.gbs, Cryologger ITB-B_Paste.gbp, Cryologger ITB-B_Silkscreen.gbo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]
2024-06-28 Add flag for RockBLOCK v3.F pin configuration
    Improved code comments. Improved Serial Monitor output. Updated libraries.
2025-02-16 Remove outdated Gerber files
    [Cryologger ITB-B_Cu.gbl, Cryologger ITB-B_Mask.gbs, Cryologger ITB-B_Paste.gbp, Cryologger ITB-B_SilkS.gbo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]
2025-02-20 Update schematics to v3.2
    [Cryologger ITB.kicad_pcb, Cryologger ITB.kicad_sch]
2025-03-28 Apply Arduino IDE 2.x auto formater
    Reformatted code using Clang 14.0.0 to align with Arduino IDE 2.x standards.
2025-03-30 Improve code commenting
    Renamed tabs. Adopted Clang 14.0.0 formatting. Simplified `myDelay` function. Changed `blinkLed` to default to LED_BUILTIN.
2025-03-31 Improve code commenting
    Added new function to display sensor measurements.
2025-03-31 Change MT-SBD validation code
    Removed battery cutoff variable and restored alarm interval variable.
2025-03-31 Create tab for IMU code
    Began adapting existing tilt-compensation code for LSM6DSOX/LIS3MDL sensor.
2025-03-31 Major updates
    Adopted Clang 14.0.0 formatting. Improved code commenting. Rearrange variable groupings. Added new user configuration section. Largely reverted main loop logic to v3.0.0 without battery cutoff.
2025-06-22 Add function to print unixtime timestamp
2025-07-17 Create case_v3.2.stl
    Added hole for micro-USB connector.
    [case_v3.2.stl]
2025-08-28 Major updates to IMU functionality
    Added 3×3 calibration, inverse soft-iron matrix. Calibration values now loaded from static .h file.
2025-08-28 Move code sections to separate .h files
    Moved Iridium union/structure to structs.h and IMU calibration values to imu_calibration.h.
2025-08-30 Add IMU calibration code
    Added code to collect raw magnetometer data, a Python script to perform an ellipsoid fit and code to test implementation.
2025-08-30 Add IMU calibration values
2025-09-04 Update IMU calibration values
2025-09-11 Cleanup to streamline repository
    [cryologger_itb_v1.csv, cryologger_itb_v1.sch, cryologger_itb_v2.csv]
2026-05-07 Remove power control from within IMU functions
2026-05-09 Remove legacy variables
    Updated debugging to display current variables.
2026-05-19 Improve sensor functionality
    Added reattempts to initialization, no-data sentinels, and constrained variables.
2026-05-24 Correct pin peripheral order
2026-06-29 Minor updates
    Added DEBUG gate to blinkLed() to save power. Disabled IMU calibration to get relative heading. Improved code comments.

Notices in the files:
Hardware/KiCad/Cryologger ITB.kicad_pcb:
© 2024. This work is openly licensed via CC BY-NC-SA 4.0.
